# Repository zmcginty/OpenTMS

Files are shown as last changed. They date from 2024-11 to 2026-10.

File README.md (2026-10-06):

# Open-Source Transcranial Magnetic Stimulator

An open-source transcranial magnetic stimulator (TMS) project, including coil designs, pulse-generator hardware, and control/charging circuitry.

> **Safety Notice**
> This is **not** a legitimate medical device and is not a substitute for real TMS treatment. This is an experiment I built in my garage, and I cannot verify that it does what it's supposed to (if anyone wants to build an open-source MRI.... let me know...) This device is dangerous, it operates at energy levels more than enough to stop your heart, kill you, blow up and do lots of damage. If you're going to play with high energy pulsed power systems; be careful.

## Table of Contents
- [TMS Coils](#tms-coils)
- [Coil Cooling](#coil-cooling)
- [Coil Materials](#coil-materials)
- [IGBT Switches](#igbt-switches)
- [Gate Drivers](#gate-drivers)
- [Measurement System](#measurement-system)
- [Charging Circuit](#charging-circuit)
- [Pulse-Generator Designs](#pulse-generator-designs)
- [Charge-Control Circuit](#charge-control-circuit)
- [Useful Resources](#useful-resources)
- [TODO](#todo)

---

## TMS Coils

I primarily build two coil geometries — single coils and figure-8 coils. What I've focused on are air-core windings in either single-layer or multi-layer form. The general architecture is adapted from research papers and the limited information published by commercial TMS coil manufacturers. The figure-8 CloudTMS coil (below) was a major influence on my designs in terms of hollow copper conductor carrying coolant.

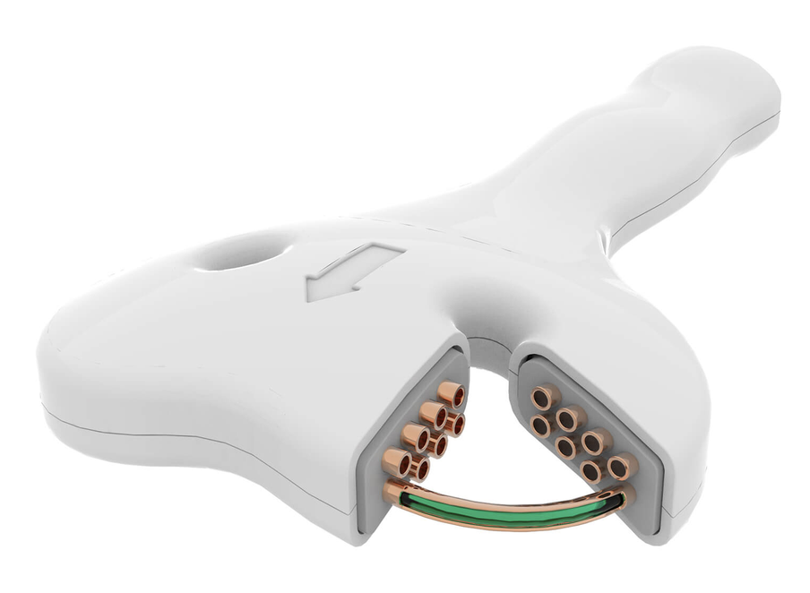
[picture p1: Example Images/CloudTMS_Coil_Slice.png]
CloudTMS coil


As I moved to higher pulse rates and energies, active cooling became necessary. My preferred approach, similar to the CloudTMS design, uses hollow copper tubing (sold for HVAC/refrigeration) insulated with PTFE heat-shrink. PTFE works well because it's a good dielectric, stays thin-walled after shrinking, tolerates high temperatures, and holds the coil shape better than thicker heat-shrink alternatives — though it does require fairly high heat to shrink fully.

**Build process:**
- Source 4mm OD / 3mm ID copper tube (5m sections) and 4.5mm, 4:1 PTFE heat-shrink in bulk.
- Feeding heat-shrink onto a long tube run takes patience — compressed air, used to create an air cushion between tube and shrink-wrap, makes this much easier.
- Wind the coil on a custom jig, either single-layer or multi-layer (multi-layer here just means winding randomly around a bobbin rather than stacking discrete single-layer coils).
- Insert something into the copper tube close to the tube's ID (weed-wacker cable works well) during the first few windings to prevent the tube from collapsing, then remove it once winding is complete.
- Hold the coil together with tape ahead of potting.

<p align="center">
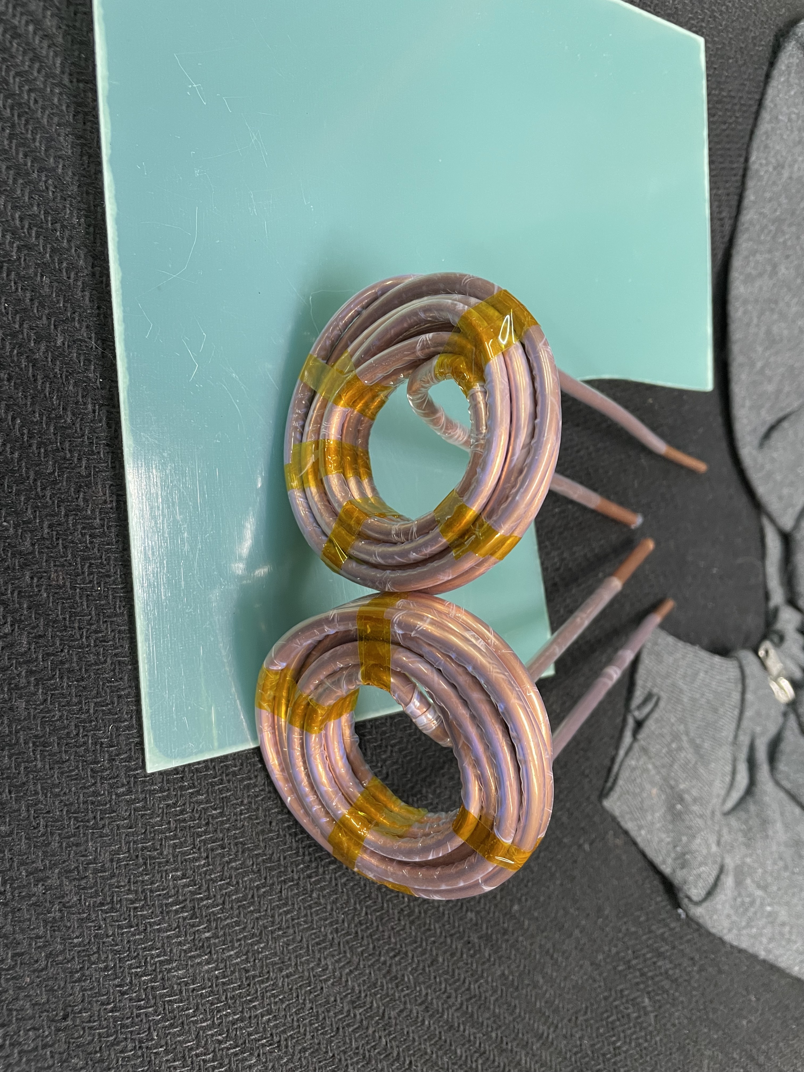
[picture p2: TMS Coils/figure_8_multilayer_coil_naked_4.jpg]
Coil before potting
  
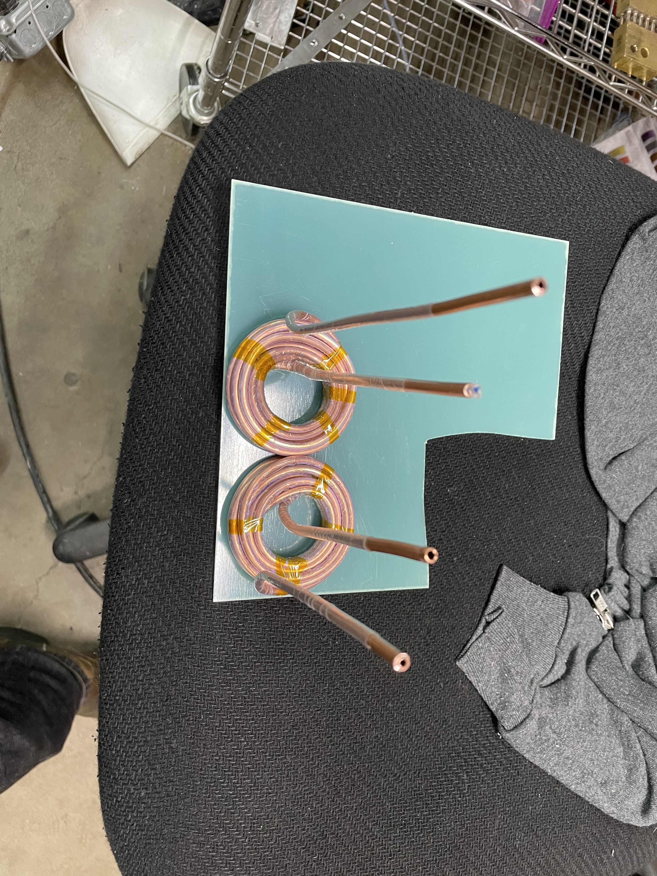
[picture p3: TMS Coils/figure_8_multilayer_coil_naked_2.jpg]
Coil before potting
  
</p>
<p align="center"><em>Example coil before potting</em></p>

Potting the coil in epoxy significantly improves mechanical stability and reduces noise by keeping the windings from moving against each other under pulse forces. Hot glue works as an alternative but produces coils that are noticeably louder in operation — not confidence-inspiring at higher power levels.

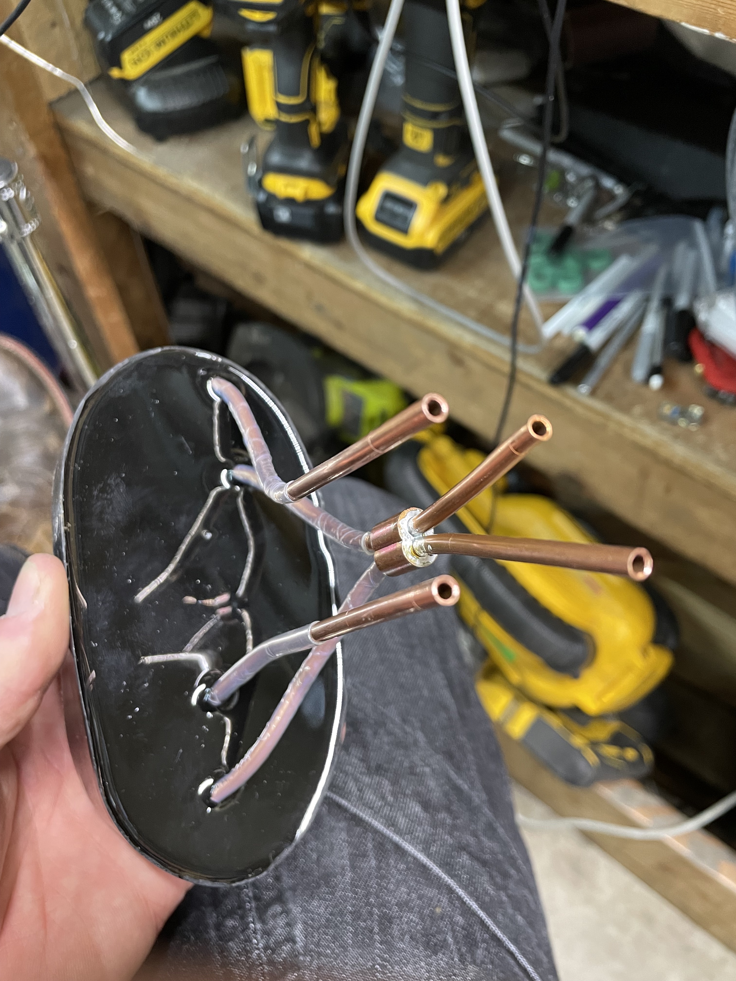
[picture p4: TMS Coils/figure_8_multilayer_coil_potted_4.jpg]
Coil after potting

<p align="center"><em>Example coil after potting</em></p>

## Coil Cooling

Coils built from hollow copper tube are cooled by pumping coolant through the winding itself.

- **Mineral oil:** Used for a long time — thinner than typical oils but thicker than water. Maintaining ~40°C required roughly 150–200 psi to push enough flow through the coil's small ID. At higher energy levels, I added a water chiller and heat exchanger to pre-cool the oil.
- **Distilled water:** More recently, I've switched to distilled water paired with a diaphragm pump, since the diaphragm provides a degree of electrical isolation between the pump mechanism and the fluid. This is simpler and more effective overall, though there is still a risk of the coolant loop reaching high voltage.

## Coil Materials

| Material | Purpose | Notes |
|---|---|---|
| [Hollow copper tube](https://www.amazon.com/dp/B082FDVNC5) | Water-cooled coil winding | Standard refrigeration-grade tube; cheap and widely available |
| [Fiberglass resin sheet](https://www.amazon.com/dp/B0DYT28W8W) | Application-side coil face | Sturdy, good electrical insulator, and appears permeable to magnetic fields — a disassembled commercial coil used what looked like FR4 fiberglass (PCB-grade) |
| [MAX EPC epoxy potting compound](https://www.amazon.com/dp/B07PMTMKZQ) | Coil potting | Inexpensive, good electrical insulator, decent thermal conductivity. For tube-cooled coils, MAX MCR (lower thermal conductivity) is also an option |

---

## IGBT Switches

My current switch of choice is the **Infineon/Eupec FZ1200R33KF2** — inexpensive and capable of handling substantial power. Prices on eBay range from ~$100–$400, and I've pushed 8kA pulses through a single unit. Adequate snubber capacitance/circuitry is essential to keep the voltage across the device under its 3.3kV rating (I target a safety margin below that).

## Gate Drivers

I've used two Power Integrations gate drivers with this IGBT:

- **2SC0535T2G0-33** — Functional, but lacks features like active clamping to protect against turn-off voltage spikes. Requires a custom PCB with gate turn-on/turn-off resistors and capacitors.
- **1SD418F2-FZ1200R33KF2** — Purpose-built for the FZ1200R33KF2; bolts directly onto the device pads. Requires only a 15VDC supply (I use a 1A source). It communicates over two fiber-optic channels (input signal and output/status), which I drive with custom PCBs using AFBR-1624Z HFBR transmitter/receiver modules, controlled by a Teensy 4.1 through a 3.3V→5V level shifter.

---

## Measurement System

### Differential Voltage Measurement
Monitoring Vce (collector-emitter voltage) across each IGBT is critical to staying within its rating — I keep a safety margin and stay below 2.5kV on 3.3kV-rated devices. Since these switches operate on the high side, measurement requires a high-voltage differential probe: I use a **Micsig DP20003** (5600V, 100MHz). A similar, lower-range HV differential probe (1300V) monitors the main capacitor bank voltage.

### Current Measurement
A shunt resistor was my first attempt but never produced a trustworthy signal. Two methods have worked well since:

1. **Rogowski coil** — Excellent for high current measurement (AC or DC, no iron core to saturate), but calibrated probes are hard to find secondhand, and a calibrated integrator circuit is needed to get a usable scope signal. I use a calibrated coil from [PowertekUK](https://powertekuk.com) — specifically the [CWTMini](https://powertekuk.com/cwtmini).
2. **Current transformer (CT)** — I use a Tektronix A621 AC current probe (rated to 2kA, available on eBay for $100–$500). In practice, it agrees with the Powertek Rogowski coil up to roughly 8kA despite the rated limit.

---

## Charging Circuit

The charging circuit is a simple, open-loop design: mains power feeds a variable transformer (variac), which drives a microwave oven transformer (MOT) to step up voltage. The stepped-up AC is rectified by a full-bridge rectifier and used to charge the main discharge capacitor bank, which is then discharged through the coil via a high-side switch (latching SCR or non-latching IGBT).

### Microwave Oven Transformers
The current two-switch flyback pulse generator uses two matched MOTs (matched by checking voltage and phase agreement between units — *measurements/resources TODO*). Drawing ~15A at 120V, two matched transformers stay below ~60°C with air cooling alone.

Earlier designs used a single MOT with low-pressure mineral-oil cooling, which worked up to ~14A — but oil cooling systems and pumps added complexity and were prone to leaks.

---

## Pulse-Generator Designs

### Design #1 — SCR-Based Pulse Generator
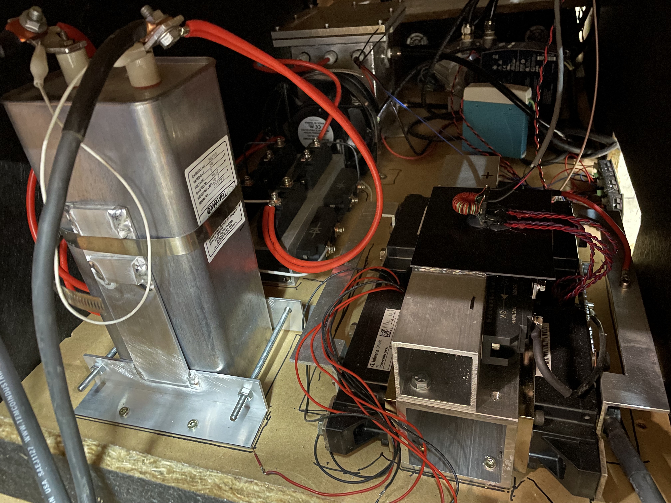
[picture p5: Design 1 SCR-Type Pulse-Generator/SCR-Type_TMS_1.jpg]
SCR switch bottom-right

<p align="center"><em>SCR-switch pulse generator (SCRs are bottom-right. Main capacitor front left. Rectifier behind capacitor. and mineral-oil cooled microwave transformer behid rectifier. </em></p>

The first design I built. It handles very high energy levels well at consistent frequencies/patterns (e.g., the standard 5Hz/10Hz protocols used in early depression-treatment research). Its limitation is pattern flexibility: an SCR/thyristor is a latching switchable diode, so once triggered it fully discharges the capacitor. This steady current decay is gentle on flyback effects but rules out more complex patterns like Theta-Burst (50Hz bursts repeating at 4–5Hz).

### Design #2 — Single-IGBT Pulse Generator
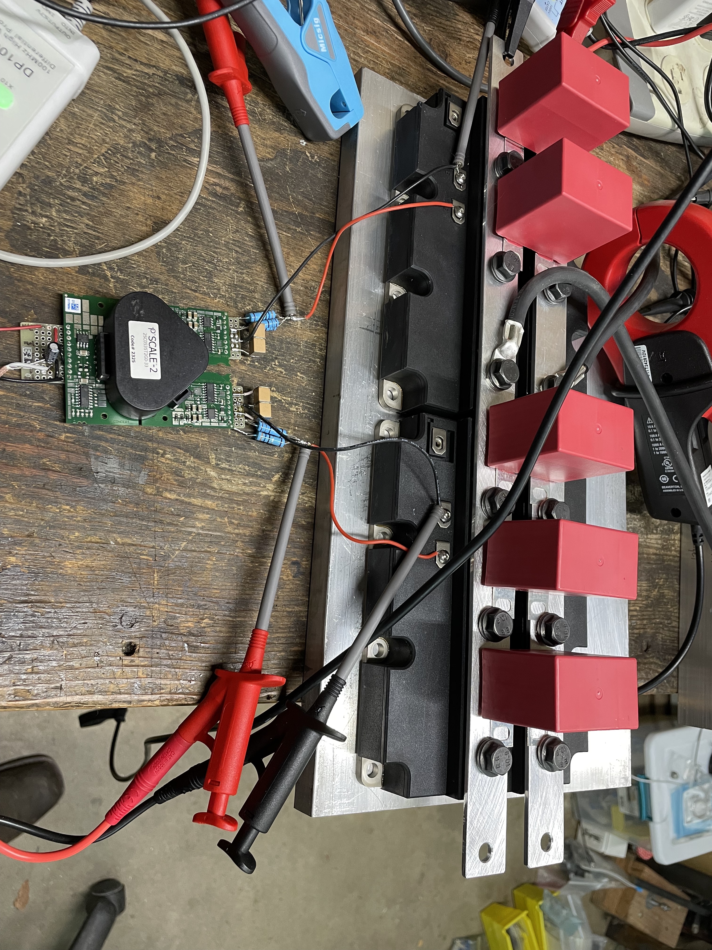
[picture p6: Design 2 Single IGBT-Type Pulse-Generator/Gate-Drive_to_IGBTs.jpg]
Single-IGBT (Two IGBTs in parallel)

<p align="center"><em>Single IGBT topology (note; two IGBTs in parallel), you can also see gate driver I used before using ones built specifically for the IGBT module</em></p>

Since IGBTs aren't latching, they can be switched on and back off within a short pulse, allowing partial capacitor discharge and enabling patterns like Theta-Burst. The tradeoff is significant flyback voltage when interrupting current through the coil — this destroyed several IGBTs before I addressed it with a robust flyback diode across the coil and snubber capacitors across the IGBT(s) to absorb spikes from parasitic wiring/busbar inductance. HV differential probes are essential here to stay within the switch's voltage rating while tuning.

This design uses a flyback diode across the coil, producing a sharp current rise but a slow fall (as flyback energy dissipates through coil/wire resistance and the diode). It worked well and was relatively simple compared to the two-switch flyback design, but since flyback energy isn't recycled, it's ultimately limited by the 120V/15A charging circuit.

### Design #3 — Two-Switch Flyback IGBT Pulse Generator
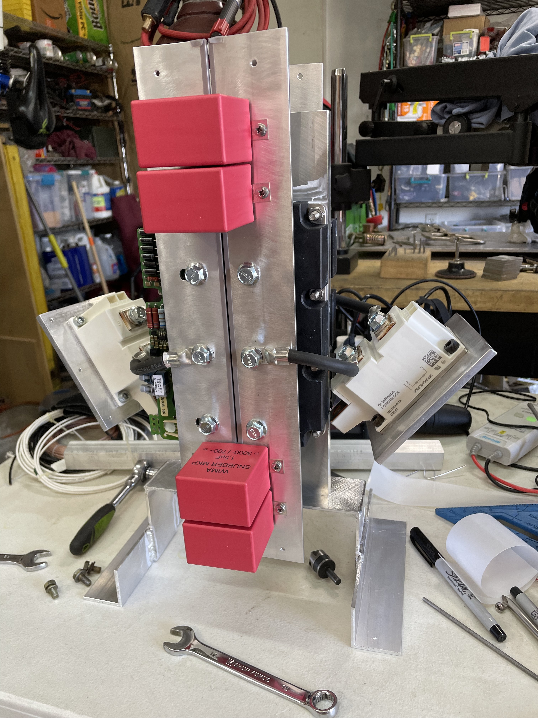
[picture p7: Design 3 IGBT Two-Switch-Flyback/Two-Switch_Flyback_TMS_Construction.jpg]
Construction of Two-Switch Flyback

<p align="center"><em>Two-Switch flyback topology being built. You can see the diodes hanging off to the sides. And gate drives are now on the left, bolted to IGBT modules behind bus-bars.</em></p>

This design recycles more pulse energy than the single-IGBT version and produces both a sharp rising *and* falling current edge, increasing di/dt for a stronger but shorter magnetic field pulse. It noticeably reduced charging-circuit current draw and appears more effective at stimulating muscle/nerve tissue than the single-switch design, even at higher peak current — likely because faster field transitions induce greater current in tissue.
+ For this design it's important to thermally bond both IGBT/switch modules so that they're the same temperature and have the same switching characteristics. For this I bolt them each to opposite sides of an aluminum plate which I attach water-cooling blocks to.
I've been realizing the importance of keeping switching loops tight, and have shortened cabling from capacitor to IGBTs, and shortening cables from IGBTs to diodes.
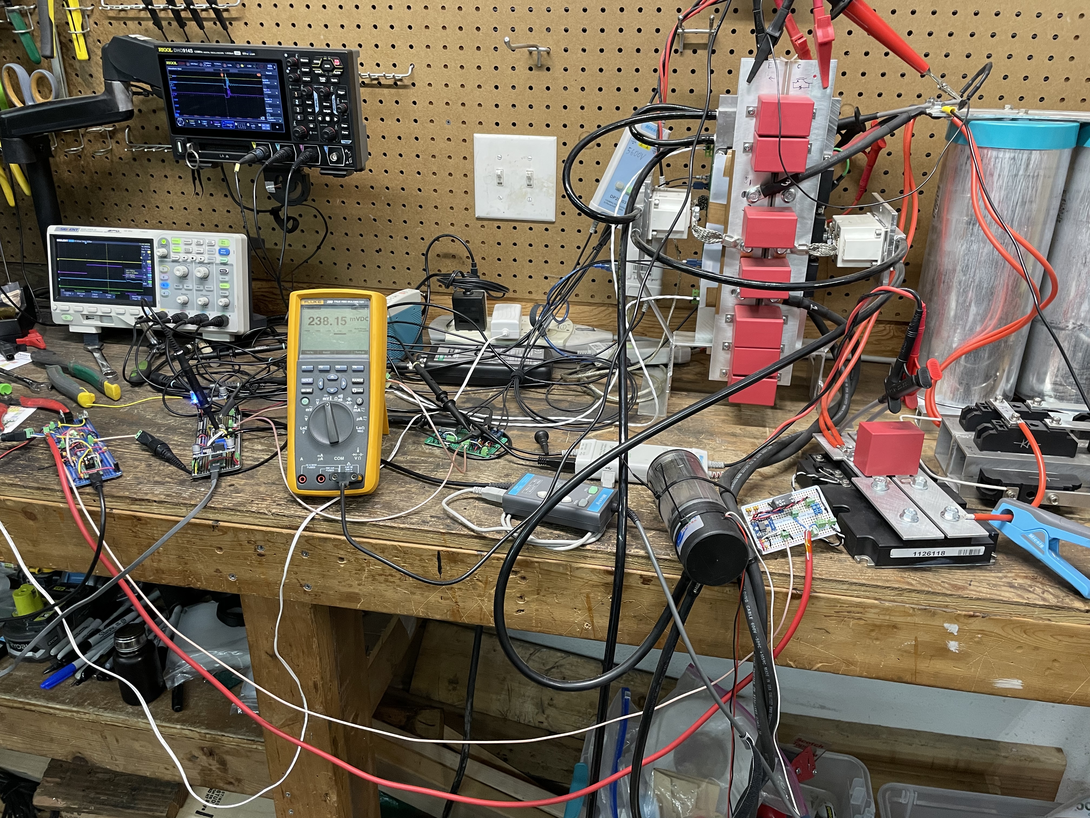
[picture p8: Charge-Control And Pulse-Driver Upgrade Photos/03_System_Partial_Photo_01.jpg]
System Photo

<p align="center"><em>Photo of the system, from left-to-right; charge-control board, multimeter, main pulse-IGBTs (with many red snubber caps), charge-control IGBT (with single red snubber in front), charge-circuit-rectifier, and main pulse capacitor bank in back </em></p>

### Design #4 — H-Bridge IGBT Pulse Generator (Not Yet Built)
Should double coil pulse current relative to the two-switch flyback topology by enabling current reversal. The complexity of positioning four large IGBT switches and the associated snubbers and diodes close to eachother, with cooling is going to be difficult without adding parasitic inductance that would offset the gains.

---

## Charge-Control Circuit
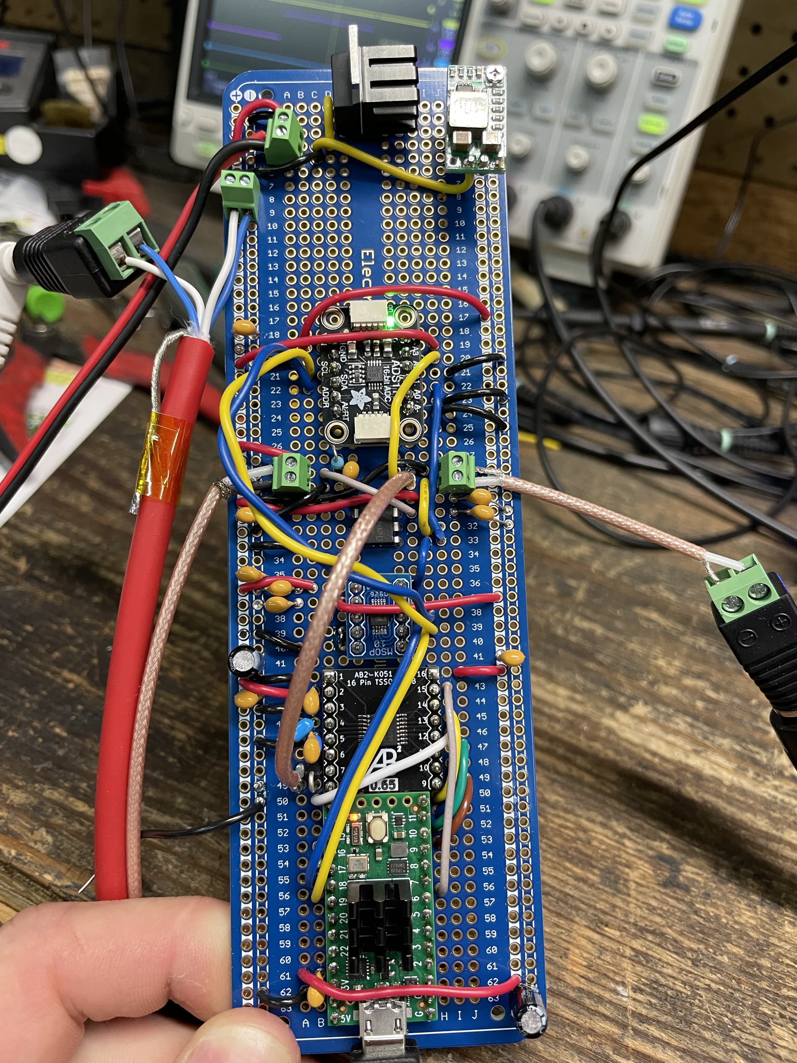
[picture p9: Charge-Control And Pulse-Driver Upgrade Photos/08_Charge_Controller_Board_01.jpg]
Newly-Built Charge-Controller Board

<p align="center"><em>Newly Built Charge-Control Board with (from bottom to top) Teensy 4.0, ADS8699 high-speed ADC, AD5693 DAC, LM393P Comparator, ADS1115 4ch slow ADC, 5V LDO, and 3.3V buck-converter</em></p>

The new charge-control system seems to be working well enough for calling it version 1!!! After many failed attempts to measure a voltage divider, and my ground plane shifting and making either the teensy and/or ADC shit itself, even after adding digital SPI isolators, I realized.... that's what HV diff probes are for! So ripped out some HV SPI/I2C isolators and I'm now just measuring the output of a Micsig 1300v diff probe. No glithes, no isolators causing signal delays, no fried chips and salsa. Perfect.

The new approach uses a DAC to output a reference voltage into a comparator, which compares it against the output of the Micsig 1300v differential probe. I have probe scale-factors in the teensy code as well as linear calibrations for both ADCs and DAC as well. I have the fast ADC on here as well incase I want to control the charge-circuit via the teensy reading ADC instead of from the comparator + DAC, but for now the comparator + DAC method is working great, so we have some extra/redundant ADCs. A weak pull-down on the DAC output ensures that if the microcontroller glitches or crashes, the DAC voltage falls to zero and the charge circuit fails safely.

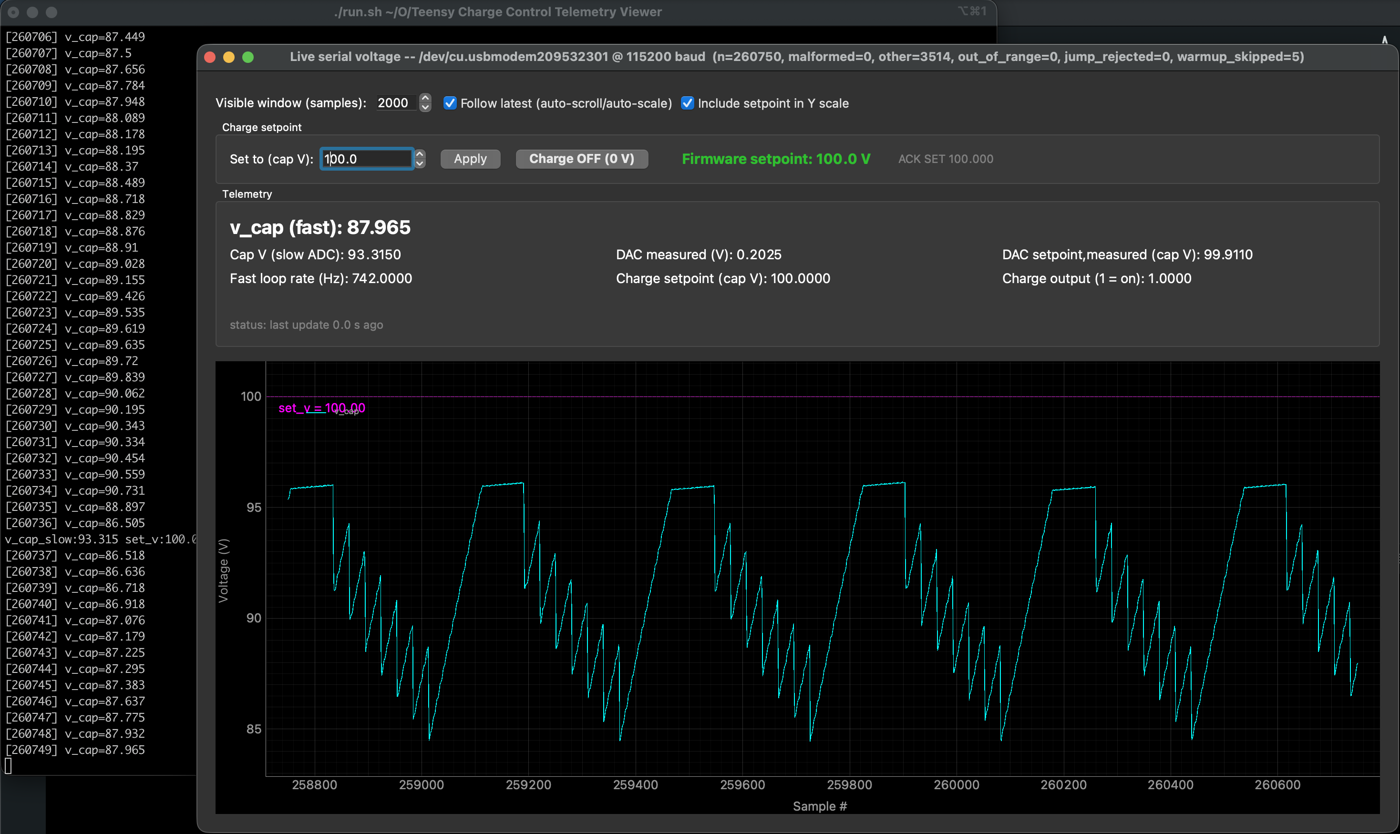
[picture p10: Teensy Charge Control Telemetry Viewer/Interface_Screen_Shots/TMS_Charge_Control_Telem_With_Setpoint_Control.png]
Python Telemetry Graph/Display

<p align="center"><em>Screenshot of a python script which displays a realtime graph and telemetry from the serial output of the teensy charge-control. Also added the ability to adjust the charge-setpoint in the python window. You can see the pulse trains as the capacitor discharges, and the charge controller working as it limits the capacitor voltage at the setpoint of (close to) 100V!</em></p>

Above is a screenshot of a python script which listens to voltage values sent over serial from the teensy charge controller and will display a live graph of the capacitor voltage, which is really useful for debugging as it's basically an autoscaling slow oscilliscope. The graph only shows the fast ADC's (ADS8699) calibrated capacitor voltage. It also displays other, slow-speed telemetry as numbers such as the slow ADC's calibrated capacitor voltage, slow ADC's measurement of DAC's output in both raw voltage, and the scaled/calibrated set-voltage it corresponds to (ie. I set the DAC to output a voltage which corresponds to 200V from the Micsig, I can verify that the ADC's measurement reads close enough, like 199.2V) I also added control to adjust the voltage setpoint from this python window which is useful for testing system starting from low voltage to be safe. I think there may be something with the comparator which is causing the cutoff to be slightly below the setpoint; in the screenshot you can see it cutting at ~95V instead of 100V. More calibrations....

## Upgrades to Pulse-Driver system
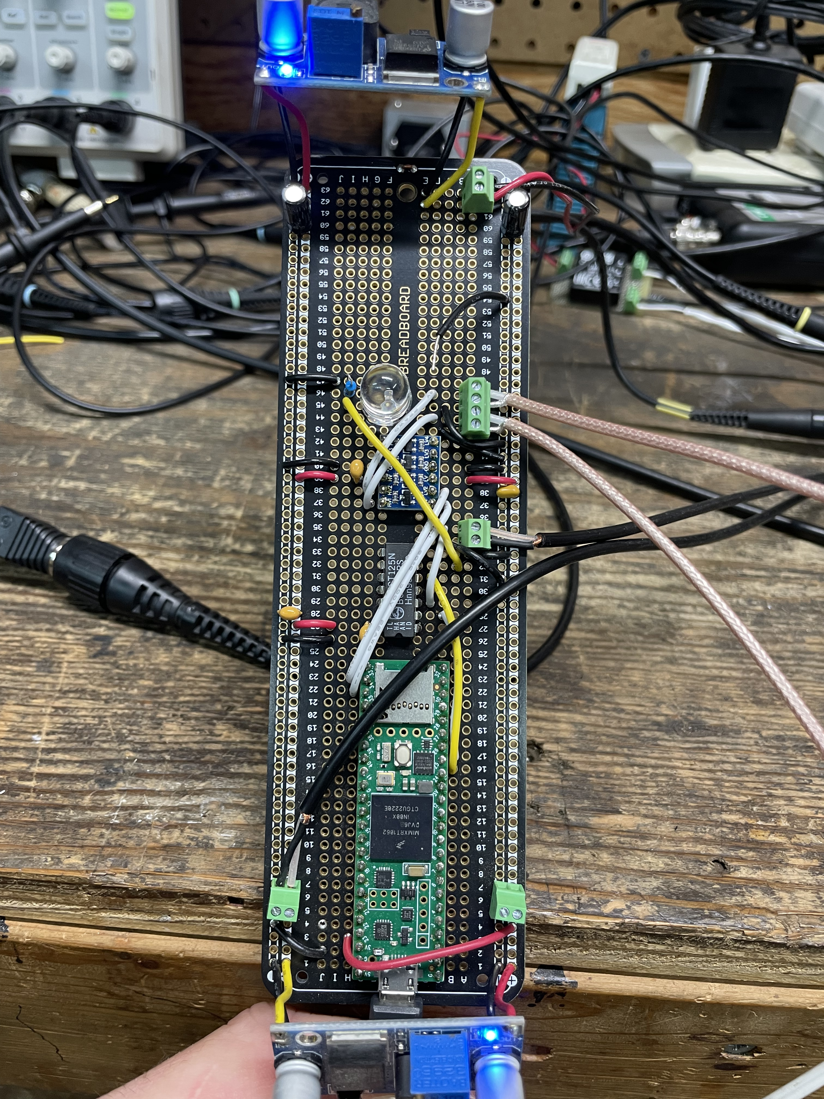
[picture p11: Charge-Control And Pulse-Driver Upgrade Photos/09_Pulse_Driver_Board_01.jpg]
Upgraded Pulse-Driver Board

<p align="center"><em>Pulse Driver Board with added inputs for RX signals from fiber-optic interface board, level-shifter and fault LED</em></p>

I've made some additions to the pulse-driver control circuit as well; for a while I was just sending pulses from the teensy to the fiber-optic transmitters to fire the IGBT switches, and not reading the signal received from the other fiber line which acknowledges the driver received each pulse, and can indicate faults like a short-circuit. I wired up the fiber RX lines, ran them through a level shifter to 3.3v for the teensy to read and the teensy is now checking that each pulse was ack'd by each gate-driver, and can turn on the big-red fault LED if something's wrong. NOTE: Big-Red Fault LED will blink if the teensy detects a warning; like a an ack pulse was slightly off, or short/long. The LED will latch on if it detects a fault such as a short-circuit. It also prints this data + occasional status out over serial. The teensy code has the ability to control a safety relay to shut off main power to the system if a fault is detected, but I don't have that safety mechanical relay wired in yet, so for now, it just keeps going.

---

## Safety Resources
- [TMS Safety with respect to seizures](https://pmc.ncbi.nlm.nih.gov/articles/PMC7732158/pdf/ndt-16-2989.pdf)
- [General article discussion factors which can decrease seizure-threshold (make it more likely you'll have a seizure)](https://www.wmchealth.org/living-well/7-everyday-factors-that-can-increase-seizure-risk)
- [Concise overview from clinic of seizure risk factors](https://www.midcitytms.com/transcranial-magnetic-stimulation-safety-with-respect-to-seizure-ndt/)

## Useful Resources

- [Online calculator used for Beam-Protocol/10-20 system to calculate position of DLPFC](https://clinicalresearcher.org/F3/calculate.php)
- [Same online calculator, where you enter your measurements](https://clinicalresearcher.org/F3/)
- [Clinical Researcher Software Tools (where I got the two links above) Contains other tools that could be useful for motor-threshold stuff](https://clinicalresearcher.org/software.htm)

## Useful Videos
- [Coil placement and the 10-20 system/beam protocol (video)](https://youtu.be/CKCvAkgdJuY?si=6TRw3_EgRK5eAh5G)
- [Same video as above with added instructions to enter measurements into clinicalresearcher calculator (link above)](https://youtu.be/akp4V5PFb6A?si=kvKB5cpgHWPCvdm8)
- [Good introductory explanation of general TMS](https://www.youtube.com/watch?v=NQHVfF_5rtc)
- [Funny video of the TMS researcher interrupting his speach with TMS](https://www.youtube.com/watch?v=85QKdt8boMA)
- [Researcher showing TMS stimulating muscles directly and muscles through the motor-cortex](https://www.youtube.com/watch?v=JA0q4fVqrFQ)
- [Good Long-Form explanation of someone who runs a TMS clinic showing how they get a patient setup, and perform treatment](https://www.youtube.com/watch?v=WxCunEG2oi0)

## TODO
1. **UPDATE THE SCHEMATICS**
2. **Refine charge-control switch** The charge controller is working well now. But I'm using a rediculously big IGBT to switch just a few tens of amps. Need to find a smaller IGBT/switch which can withstand ~2-3kV.
3. **Build a phase-control rectifier** to replace the HV charge circuit's current rectifier and eliminate the variac, integrating it into the charge system. May need PID-style control of phase/firing angle — or a simpler bang-bang control scheme.
4. **Process gate-driver fault feedback** Reading status/feedback from gate-drivers is working now and has latching/blinking LEDs/indicators to indicate warnings and faults. There is functionality to turn off a safety relay, disconnecting power from a subsystem or whole system which I'll get wired up later.
5. **Add functionality to Pulse-Driver** To run different patterns/protocols, maybe add input (with damn good shielding) so user can press a button to fire a single pulse.
6. **Finally build a tool to map the magnetic field strength & shape of a coil.** My idea is basically put a precise analog hall-effect sensor on some 3d gantry machine like a 3d printer, and have it scan over many 3d points around the coil and create a 3d heat-map of magnetic field strength. Anyone know how to use 3d-printers? and know how to make them scan some end-effector to create a map like this???? I'd love some help!

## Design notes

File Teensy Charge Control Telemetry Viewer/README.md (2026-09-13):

This is a sub-project of the pulse-generator; a charge controller arduino sketch for reading an ADC to read divided capacitor voltage, and toggling an output to turn on or off the charge circuit. No fancy porpotional control yet...

There's also a python script which takes in voltage values from a serial port and plots them using pyqtgraph lib in real-time and can log data for analysis. This is basically for tuning the ADC system given how noisy the environment is around this pulse-generator. So it allows me to tune how I average ADC samples and so on, so I don't get any major jumps or noise.

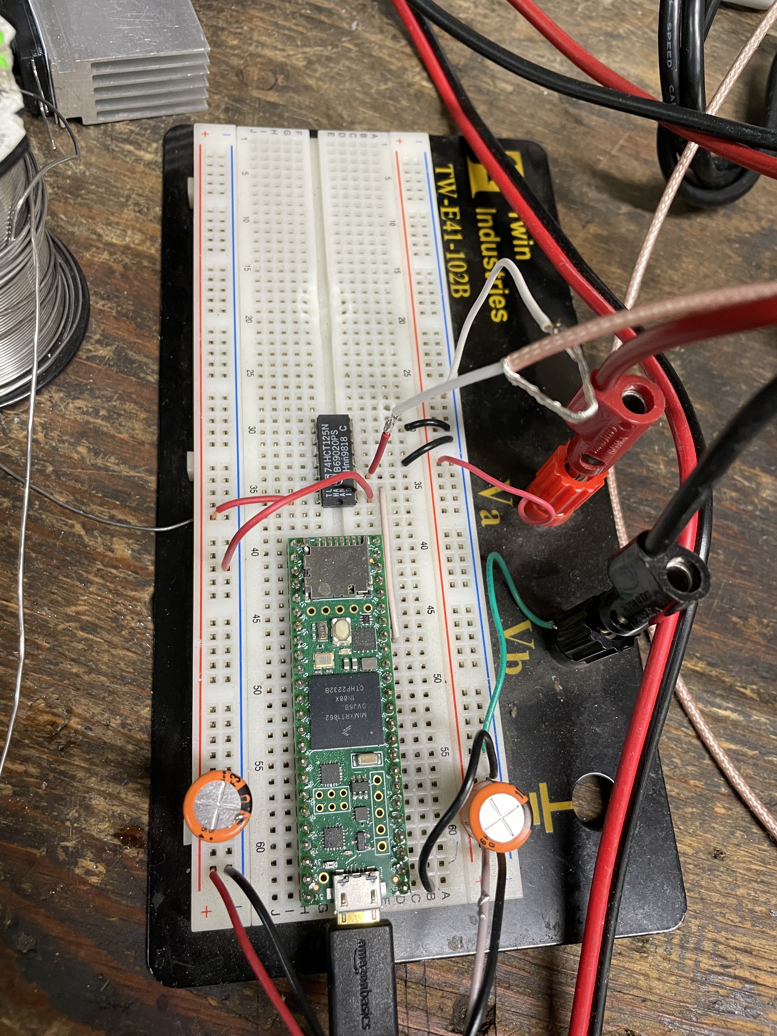
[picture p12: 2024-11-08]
Design 2 Single IGBT-Type Pulse-Generator/Teensy_Pulse-Gen_with_Level_Shift_2.jpg

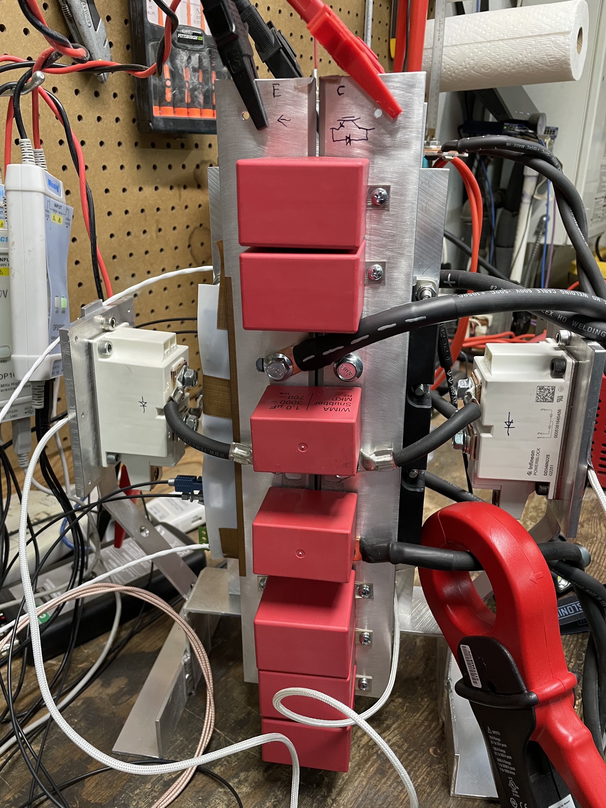
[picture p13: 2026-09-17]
Design 3 IGBT Two-Switch-Flyback/Two_Switch_Flyback_TMS_1.jpg

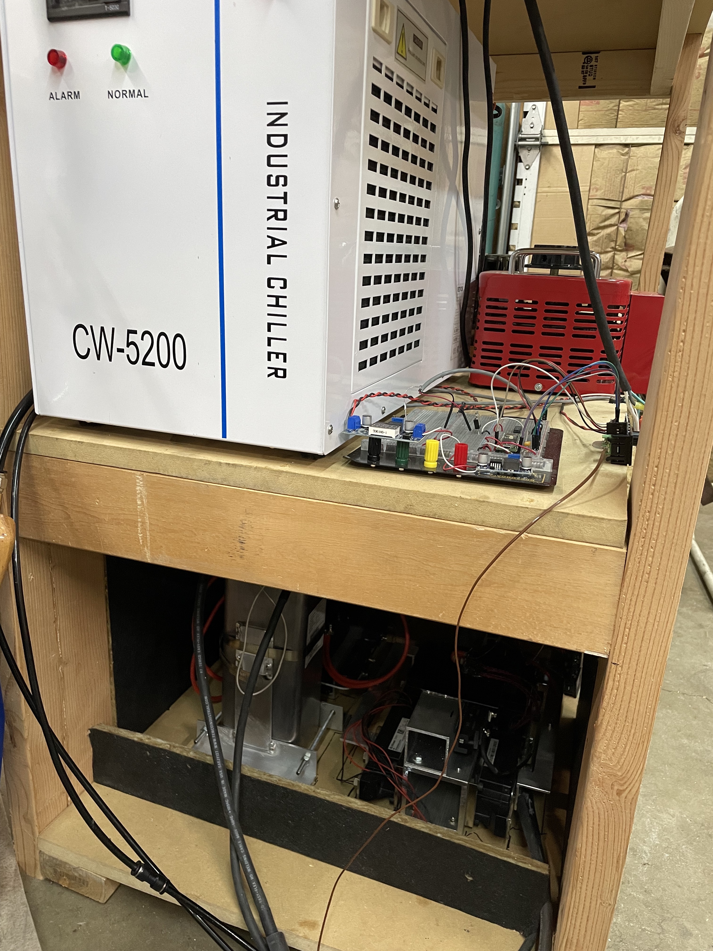
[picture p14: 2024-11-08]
Design 1 SCR-Type Pulse-Generator/SCR-Type_TMS_Power_Cooling_Control.jpg

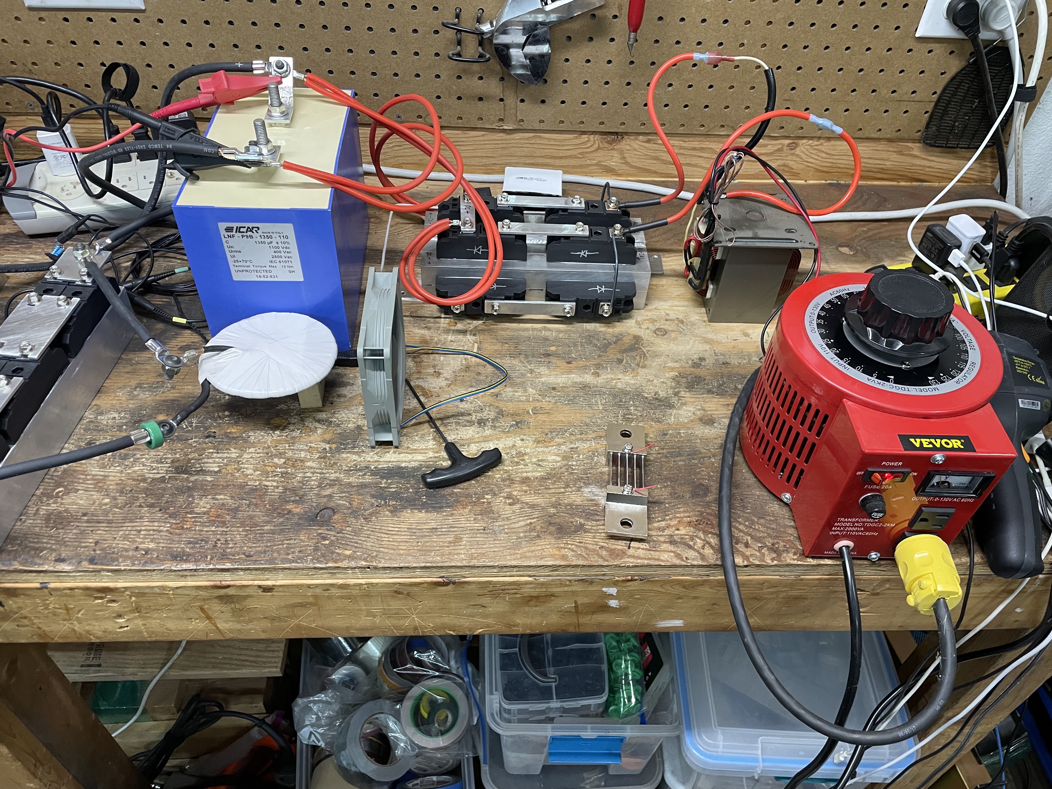
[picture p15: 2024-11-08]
Design 2 Single IGBT-Type Pulse-Generator/Charging_Circuit_1.jpg

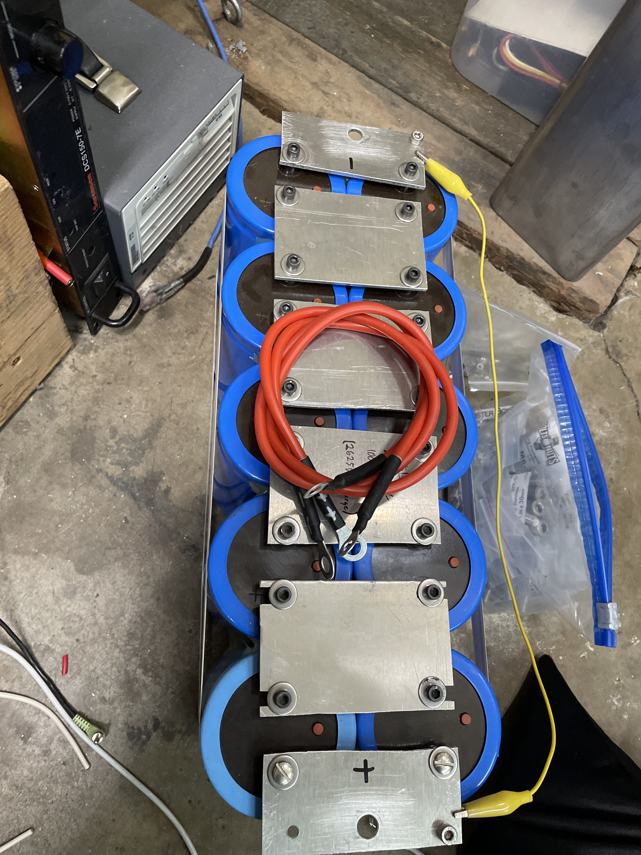
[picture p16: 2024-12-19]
Design 2 Single IGBT-Type Pulse-Generator/electrolyt_cap_bank.jpg

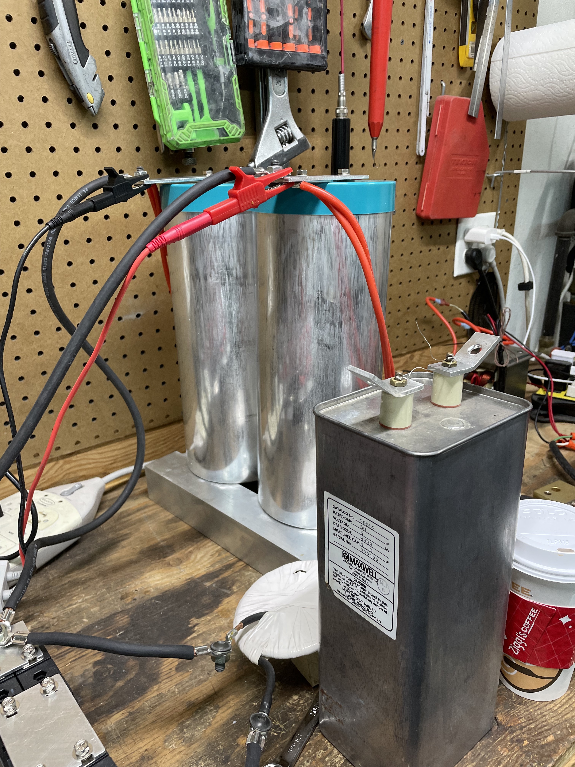
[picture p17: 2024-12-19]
Design 2 Single IGBT-Type Pulse-Generator/4kv_oil_cap_next_to_1800v_film_caps.jpg

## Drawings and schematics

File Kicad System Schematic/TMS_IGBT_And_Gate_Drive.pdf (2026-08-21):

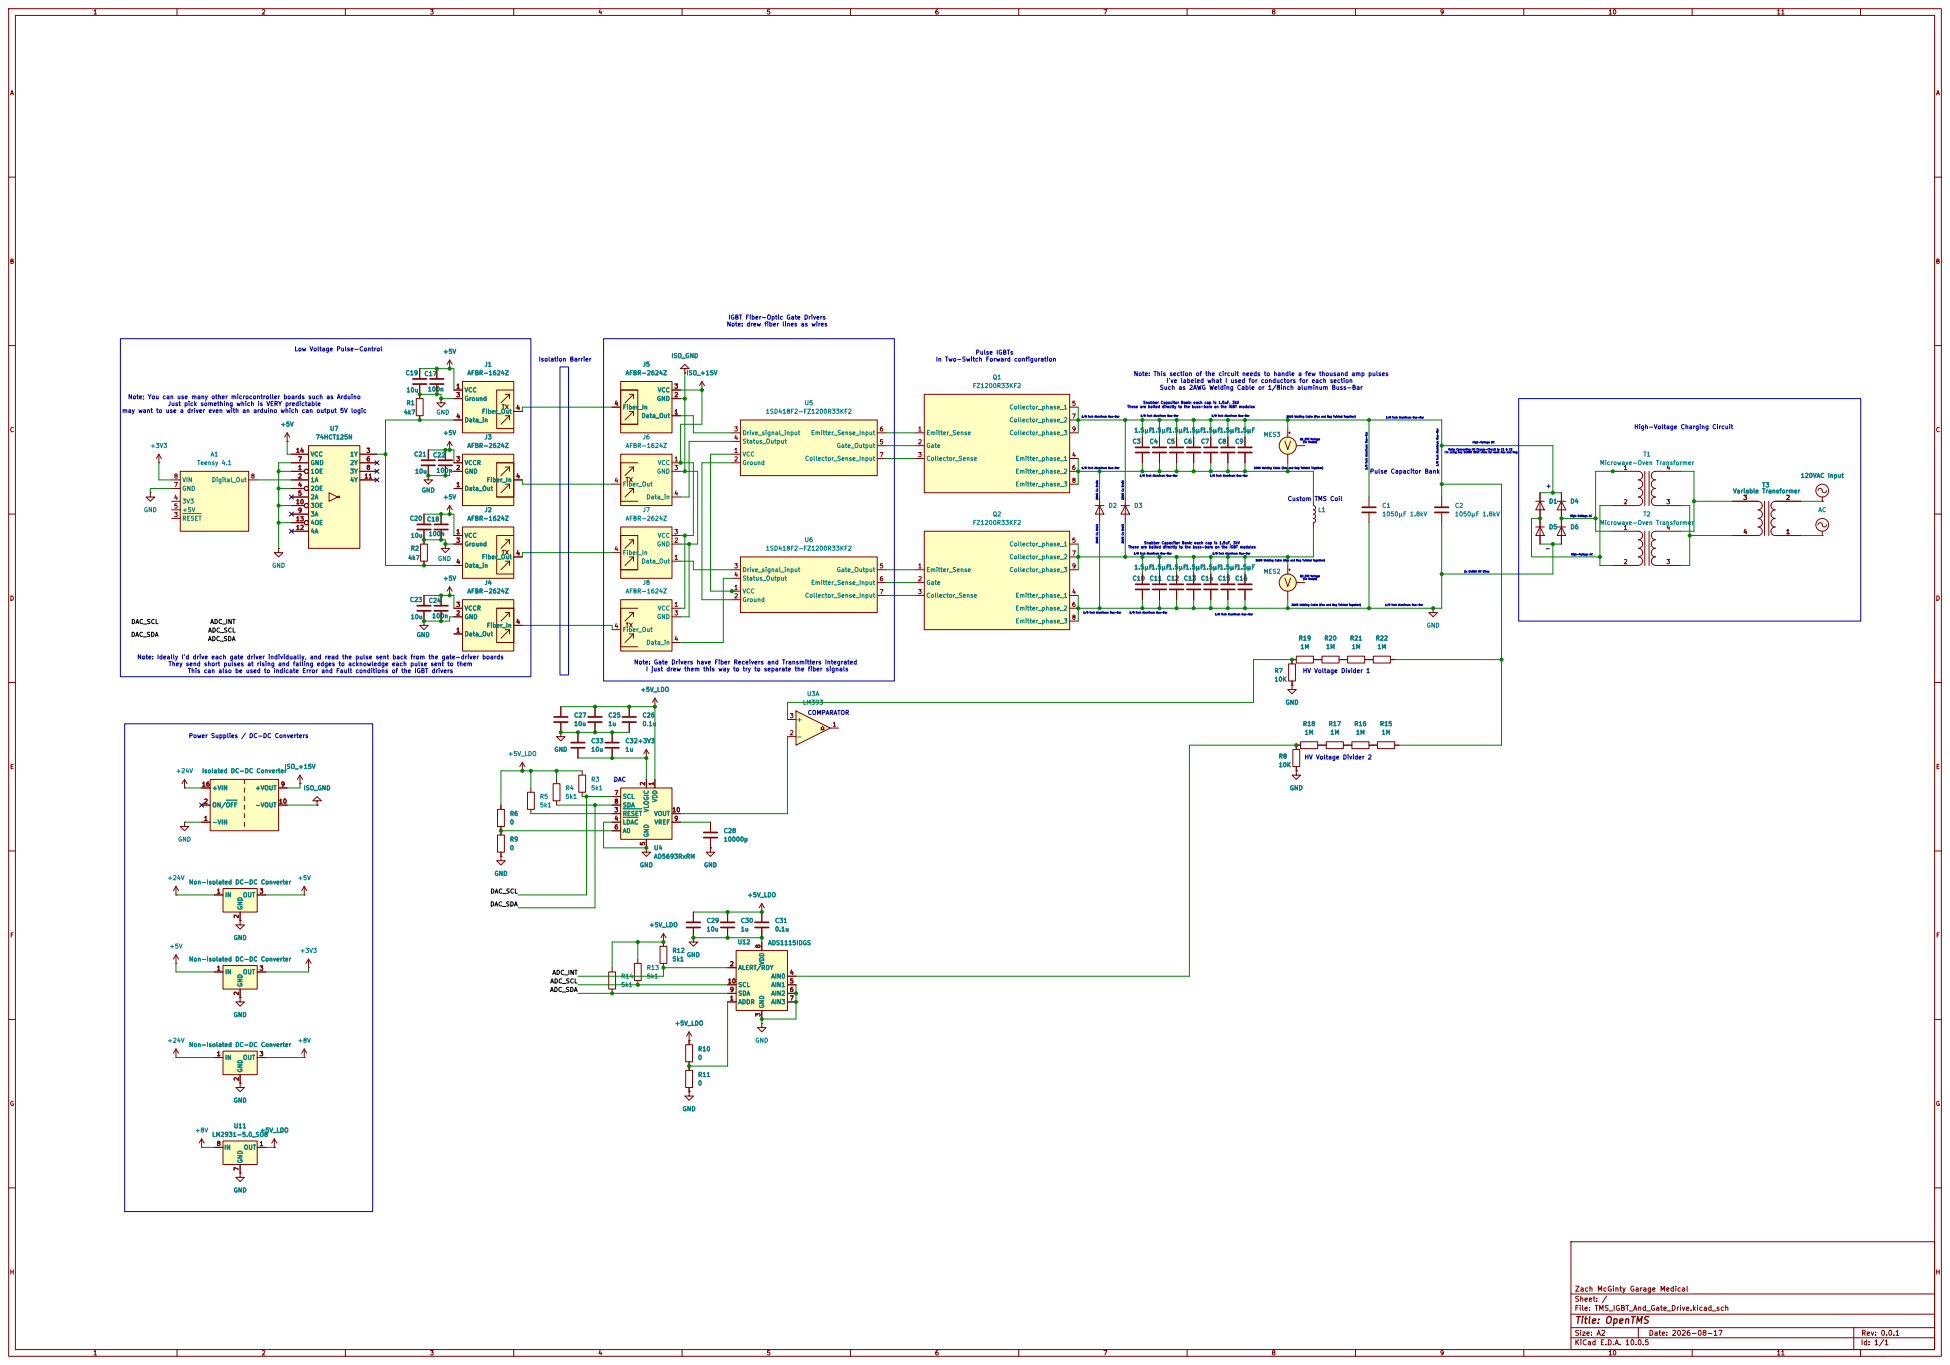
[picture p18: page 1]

IGBT Fiber-Optic Gate Drivers Note: drew fiber lines as wires
AFBR-2624Z R6

1/8 inch Aluminum Bus-Bar Pulse Capacitor Bank1/8 inch Aluminum Bus-Bar 1/8 inch Aluminum Bus-Bar Isolation Barrier

1/8 inch Aluminum Bus-Bar Note: This section of the circuit needs to handle a few thousand amp pulses

I've labeled what I used for conductors for each section Such as 2AWG Welding Cable or 1/8inch aluminum Buss-Bar

1/8 inch Aluminum Bus-Bar Note; You can use many other microcontroller boards such as Arduino
Just pick something which is VERY predictable may want to use a driver even with an arduino which can output 5V logic

These are bolted directly to the buss-bars on the IGBT modules

2AWG Welding Cable (Pos and Neg Twisted Together) Snubber Capacitor Bank; each cap is 1.5uF, 3kV

High-Voltage DC Note: Connecting HV Charge-Circuit to C1 & C2

I'm using two 14AWG 30kV wires for each Pos and Neg Note: Ideally I'd drive each gate driver individually, and read the pulse sent back from the gate-driver boards

T2 Microwave-Oven Transformer GND

High-Voltage AC Q2 Diff Voltage

2 OUT 3 Non-Isolated DC-DC Converter V

2AWG Welding Cable (Pos and Neg Twisted Together) Note: Gate Drivers have Fiber Receivers and Transmitters Integrated

They send short pulses at rising and falling edges to acknowledge each pulse sent to them

This can also be used to indicate Error and Fault conditions of the IGBT drivers

2 OUT 3 Non-Isolated DC-DC Converter R16

GND Non-Isolated DC-DC Converter

Isolated DC-DC Converter

2 OUT 3 GND Non-Isolated DC-DC Converter

2 OUT 3 Non-Isolated DC-DC Converter +5V_LDO C31

IN 8 Non-Isolated DC-DC Converter

Zach McGinty Garage Medical
Sheet: /
File: TMS_IGBT_And_Gate_Drive.kicad_sch
Title: OpenTMS

Size: A2 | Rev: 0.0.1
KiCad E.D.A. 10.0.5 | Id: 1/1

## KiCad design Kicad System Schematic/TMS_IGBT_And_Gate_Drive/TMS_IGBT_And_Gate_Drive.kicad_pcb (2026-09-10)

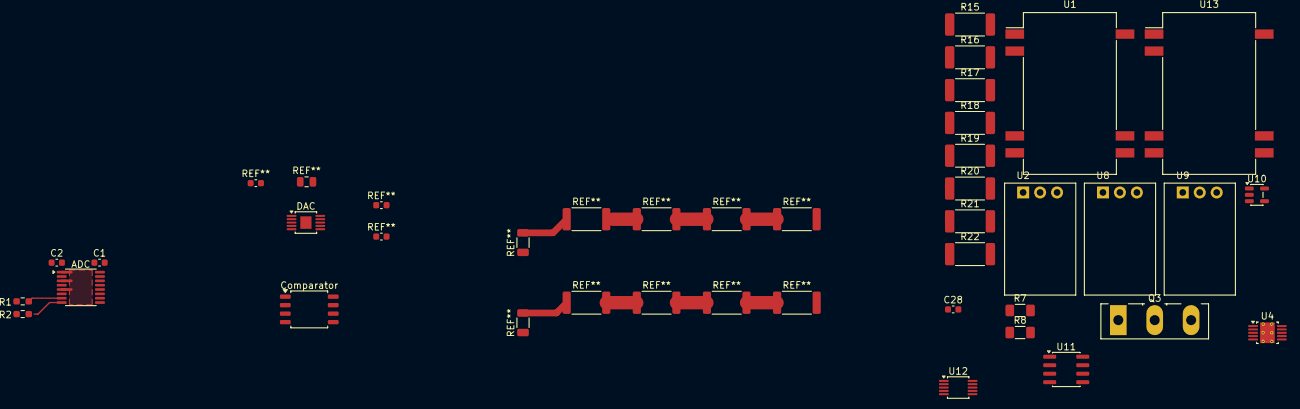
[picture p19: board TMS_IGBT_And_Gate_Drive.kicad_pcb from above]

Board: 2 copper layers, 28 parts (0 on the bottom side), 15 nets.

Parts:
ADC: ADS8699IPWR; TSSOP-16_4.4x5mm_P0.65mm
C1, C2: C_0603; C_0603_1608Metric
C28: 10000p; C_0603_1608Metric
Comparator: LM293DR; SOIC-8_5.3x5.3mm_P1.27mm
DAC: AD5683RARMZ; MSOP-10-1EP_3x3mm_P0.5mm_EP1.68x1.88mm
Q3: IRG4PF50W; TO-247-3_Vertical
R1, R2: R_0603_1608Metric_Pad0.98x0.95mm_HandSolder
R7, R8: 10K; R_1206_3216Metric_Pad1.30x1.75mm_HandSolder
R15, R16, R17, R18, R19, R20, R21, R22: 1M; R_2512_6332Metric_Pad1.40x3.35mm_HandSolder
U1, U13: Isolated DC-DC Converter; Converter_DCDC_Artesyn_ATA_SMD
U2, U8, U9: Non-Isolated DC-DC Converter; Converter_DCDC_Murata_OKI-78SR_Horizontal
U4: AD5693RxRM; AD5683RARMZ
U10: MCP1415; SOT-23-5
U11: LM2931-5.0_SO8; SOIC-8_3.9x4.9mm_P1.27mm
U12: ADS1115IDGS; TSSOP-10_3x3mm_P0.5mm

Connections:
+5V: U2.3 (OUT), U8.1 (IN)
+8V: U9.3 (OUT), U11.8 (IN)
+24V: U1.16 (+VIN), U2.1 (IN), U9.1 (IN), U13.16 (+VIN)
GND: C28.2, Q3.2 (C), R7.1, R8.1, U1.1 (-VIN), U2.2 (GND), U8.2 (GND), U9.2 (GND), U11.2 (GND), U11.3 (GND), U11.6 (GND), U11.7 (GND), U12.3 (GND), U12.5 (AIN1), U12.6 (AIN2), U12.7 (AIN3), U12.8 (VDD), U13.1 (-VIN)
ISO_+15V: U1.9 (+VOUT), U10.2 (Vdd), U13.9 (+VOUT)
ISO_GND: U1.10 (-VOUT), U10.4 (GND), U13.10 (-VOUT)
unnamed: R15.2, R22.2
unnamed: R15.1, R16.2
unnamed: R16.1, R17.2
unnamed: R17.1, R18.2
unnamed: R19.2, R20.1
unnamed: R20.2, R21.1
unnamed: R21.2, R22.1
unnamed: R7.2, R19.1
unnamed: R8.2, R18.1, U12.4 (AIN0)

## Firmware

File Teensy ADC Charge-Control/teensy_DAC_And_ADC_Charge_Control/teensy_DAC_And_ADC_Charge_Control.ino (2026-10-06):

/*
  OpenTMS Charge_Control, built to run on Teensy 4.0
    ADS8699 18-bit SAR fast ADC for reading capacitor voltage through Micsig Active H.V. Differential Probe
    AD5693 16-bit DAC outputs analog signal to comparator, which compares DAC output to voltage from Micsig H.V. Diff Probe (capacitor voltage)
    ADS1115 16-bit Sigma-Delta slow ADC for verifying DAC output, and as another redundant reading of Micsig H.V. Diff Probe (capacitor voltage)

  This control system can either
    1. Directly control connecting/disconnecting the capacitor's charge circuit by reading the capacitor's voltage, and turning off charge-circuit when it gets above a set threshold
    2. Or by outputting an analog signal via the AD5693 DAC which a comparator compares to the capacitor's voltage. I beleive the comparator is more robust and fail-safe.

  CHARGE SETPOINT (settable over Serial):
    One setpoint, in capacitor volts, drives both methods: the DAC/comparator
    threshold and the direct ADC control. It starts at 0 V (charging disabled)
    on every boot and can never exceed SETPOINT_MAX_V.
    Commands (one per line, case-insensitive):
      SET <volts>   set the charge setpoint, e.g. "SET 800"
      OFF           setpoint to 0 V (charging disabled)
      GET           report the current setpoint
      AVG <n>       ADS8699 averaging depth (NUM_AVG)
    Replies: "ACK SET 800.000", "ACK AVG 500", or "ERR <reason>".
    The status line also reports the active setpoint as "set_v:<volts>".

  LOOP STRUCTURE (cooperative multi-rate scheduling, no threads):
    - FAST path, every loop():  ADS8699 averaged read -> direct charge control.
    - SLOW paths, non-blocking, each on its own timer:
        dac_service()     -- writes the AD5693 only when the target code changes.
        ads1115_service() -- state machine: starts a conversion, comes back
                             later to collect it. Never waits on the ADC.
        command_service() -- reads serial commands, never blocks.
        print_service()   -- rate-limited Serial output.
    Each slow task does at most ONE short I2C transaction per loop() pass,
    so the fast path is never stalled for more than ~100-200 us by I2C.
*/

#include <SPI.h>
#include "Adafruit_AD569x.h"
#include <Wire.h>
#include <Adafruit_ADS1X15.h>

Adafruit_ADS1115 ads;
Adafruit_AD569x ad5693; // Create an object of the AD5693 library

const uint8_t DEBUG = 0;
const uint8_t CALIBRATION_MODE = 0;

// ---------- User configuration ----------
const uint8_t PIN_CS   = 10;   // CONVST/CS pin (any digital GPIO)
const uint8_t PIN_RST  = 9;    // RST pin (optional but recommended)
const uint8_t PIN_RVS  = 6;    // RVS (conversion-ready status) pin
const uint8_t PIN_CHRG_CTRL  = 5;    // charge control output pin

// SPI clock: datasheet allows up to 66.67 MHz for SPI
const uint32_t SPI_CLOCK_HZ =   40000000; // 40 MHz

SPISettings adsSPISettings(SPI_CLOCK_HZ, MSBFIRST, SPI_MODE0);

// Timing from the datasheet (Timing Requirements: Conversion Cycle,
// ADS8699 row): tconv = 5000 ns max. Used only as a safety-timeout
// ceiling for the RVS poll below now, not as the wait time itself.
const uint16_t T_CONV_US = 7;   // >= 5 us conversion time + margin
const uint16_t RVS_TIMEOUT_US = 50; // generous safety net; real tconv is ~5us

// ---------- Charge setpoint ----------
// Hard ceiling for SET commands. Set this to what your capacitor bank,
// IGBTs and probe (1300 V max) can safely take; anything above it is refused.
const float SETPOINT_MAX_V = 1000.0f;
// Setpoints below this count as "charging disabled": DAC at 0 V and the
// direct-control output held LOW.
const float SETPOINT_MIN_ACTIVE_V = 1.0f;
// The active setpoint in capacitor volts. Always starts at 0 V on boot.
// Change it with the SET command, not by editing this line.
float chargeSetpointV = 0.0f;

// If a value is below -10v, ignore it and wait for the next one...
const float MIN_VOLTAGE_THRESHOLD = -10;

// ---------- ADS8699 averaging configuration ----------
// NUM_AVG sets the fast control loop's latency: each batch takes roughly
// NUM_AVG x (one conversion + SPI read). Lower = faster cutoff response.
uint16_t NUM_AVG = 500;
const uint16_t NUM_AVG_MIN = 1;
const uint16_t NUM_AVG_MAX = 20000; // sanity ceiling for the 64-bit accumulator / loop time

// ---------- Slow-task rates ----------
// ADS1115: one "sweep" = one conversion on every channel in ADS1115_CHANNELS.
// Sweeps start at ADS1115_SWEEP_HZ; ADS1115_AVG sweeps are averaged before
// a new value is published (published rate = ADS1115_SWEEP_HZ / ADS1115_AVG).
uint16_t ADS1115_SWEEP_HZ = 100;
uint16_t ADS1115_AVG = 10;               // -> 10 Hz published, each a 10-sample average
// At 860 SPS a conversion takes ~1.16 ms; we don't touch the bus until this has passed.
const uint32_t ADS1115_CONV_WAIT_US = 1300;

uint16_t PRINT_HZ = 10;                  // Serial output rate
const uint32_t DAC_RETRY_MS = 100;       // retry interval if a DAC write fails

// ---------- ADS1115 channel map ----------
const uint8_t ADS1115_CHANNELS[] = {1, 3};
const uint8_t ADS1115_NUM_CH = sizeof(ADS1115_CHANNELS);
const uint8_t ADS1115_CH_DAC   = 1;
const uint8_t ADS1115_CH_PROBE = 3;

// ---------- DAC configuration ----------
float vref = 2.5000;
uint8_t gain = 2;   // gain of 2 means our span is 0-5V
// Target DAC output voltage (what the comparator sees). Set from the charge
// setpoint by applySetpoint(); dac_service() only writes to the chip when
// the resulting code changes.
float dacTargetVolts = 0.00f;
const float DAC_VERIFY_TOL_V = 0.010f;   // ADS1115 readback must be within this of the commanded voltage

// ADS8699 Calibration of ADC input voltage to calibrated multimeter
// Y = 0.9997*X + 9.895e-005 (cal performed 10/2/2026)
const float ADS8699_CAL_OFFSET = 0.00009895;
const float ADS8699_CAL_SCALE = 0.9997;

// ADS1115 Calibration of ADC input voltage to calibrated multimeter
//  Y = 1.000*X + 0.001057 (cal performed 10/2/2026)
const float ADS1115_CAL_OFFSET = 0.001057;
const float ADS1115_CAL_SCALE = 1.000;

// Probe Multiplier; used for measuring active HV differential probes.
// For measuring capacitor voltage, I'm using a 1300V diff probe with a multiplier of 500X
const uint16_t PROBE_MULTIPLIER = 500;

// Calibration for actual measured capacitor voltage
// Y = 0.9854*X + 0.1270
const float VDIV_CAL_OFFSET = 0.127;
const float VDIV_CAL_SCALE = 0.9854;

// ---------- Input range table (Table 7-3 / 7-4, VREF = 4.096 V) ----------
// (Kept above the first function: the Arduino IDE inserts auto-generated
// prototypes just before the first function, so custom types used in
// function signatures must be defined before it.)
enum ADS8699_Range : uint8_t {
  RANGE_PM_3VREF    = 0b0000, // ±12.288 V
  RANGE_PM_2p5VREF  = 0b0001, // ±10.24 V
  RANGE_PM_1p5VREF  = 0b0010, // ±6.144 V
  RANGE_PM_1p25VREF = 0b0011, // ±5.12 V
  RANGE_PM_0p625VREF= 0b0100, // ±2.56 V
  RANGE_0_3VREF     = 0b1000, // 0 to 12.288 V
  RANGE_0_2p5VREF   = 0b1001, // 0 to 10.24 V
  RANGE_0_1p5VREF   = 0b1010, // 0 to 6.144 V
  RANGE_0_1p25VREF  = 0b1011  // 0 to 5.12 V
};

// Positive/negative full-scale voltages for each range, VREF = 4.096 V
struct RangeInfo { float negFS; float posFS; };

///////////////////////////////////////////////////////////////////////////////
// SHARED STATE FOR SLOW TASKS
// (globals declared before any function that uses them)

// Latest published ADS1115 readings, calibrated, indexed by AIN number.
float ads1115_volts[4] = {0.0f, 0.0f, 0.0f, 0.0f};
bool ads1115_haveData = false;   // true once the first averaged set has been published
bool ads1115_newData = false;    // set on each publish, cleared by the consumer in loop()

int32_t lastDacCodeWritten = -1; // -1 = nothing written yet
bool dacSkipNextVerify = true;   // skip the averaging window that straddles a DAC change
bool dacVerifyOk = false;
float dacVerifyErrorV = 0.0f;

bool chargePinOn = false;        // last level written to PIN_CHRG_CTRL (for the status line)

///////////////////////////////////////////////////////////////////////////////
// AD5693 DAC FUNCTIONS
uint16_t voltageToDacCode(float voltage, float vref, uint8_t gain) {
  float maxCode = 65536.0;
  float code = (voltage / (vref * gain)) * maxCode;
  if (code > 65535.0) code = 65535.0;
  if (code < 0.0) code = 0.0;
  return (uint16_t)code;
}

// Inverse of voltageToDacCode(): the voltage the DAC should output for a given code.
float codeToVoltage(uint16_t code, float vref, uint8_t gain) {
  return vref * gain * ((float)code / 65536.0);
}

// Converts a desired capacitor voltage into the probe-output voltage the
// comparator should trip at (i.e. the DAC target), by inverting the probe
// multiplier and the probe calibration used for v_cap in loop().
// The DAC's own accuracy isn't calibrated here -- that's what the ADS1115
// verification is for.
float capVoltToDacVolts(float capVolts) {
  float v_div = (capVolts - VDIV_CAL_OFFSET) / VDIV_CAL_SCALE;
  return v_div / (float)PROBE_MULTIPLIER;
}

// Writes the DAC only when the target code differs from what was last
// successfully written. On failure, retries no more often than DAC_RETRY_MS
// so a disconnected DAC can't flood the bus or Serial.
void dac_service() {
  static elapsedMillis sinceFail = DAC_RETRY_MS;

  uint16_t code = voltageToDacCode(dacTargetVolts, vref, gain);
  if ((int32_t)code == lastDacCodeWritten) return;
  if (sinceFail < DAC_RETRY_MS) return;

  if (ad5693.writeUpdateDAC(code)) {
    lastDacCodeWritten = code;
    dacSkipNextVerify = true;   // the next published ADS1115 average may include pre-change samples
  } else {
    sinceFail = 0;
    Serial.println("Failed to update DAC.");
  }
}

// Compares the ADS1115's DAC-channel reading with the commanded DAC
// voltage. Called whenever a new averaged ADS1115 set is published.
void dac_verify() {
  if (lastDacCodeWritten < 0) { dacVerifyOk = false; return; }
  if (dacSkipNextVerify) { dacSkipNextVerify = false; return; }

  float expected = codeToVoltage((uint16_t)lastDacCodeWritten, vref, gain);
  dacVerifyErrorV = ads1115_volts[ADS1115_CH_DAC] - expected;
  dacVerifyOk = fabsf(dacVerifyErrorV) <= DAC_VERIFY_TOL_V;
}

///////////////////////////////////////////////////////////////////////////////
// CHARGE SETPOINT

bool chargeEnabled() {
  return chargeSetpointV >= SETPOINT_MIN_ACTIVE_V;
}

// The only place the setpoint changes. Updates the DAC target too, so the
// comparator and the direct control always use the same value.
void applySetpoint(float capVolts) {
  if (!(capVolts >= 0.0f)) capVolts = 0.0f;            // also catches NaN
  if (capVolts > SETPOINT_MAX_V) capVolts = SETPOINT_MAX_V;
  chargeSetpointV = capVolts;
  dacTargetVolts = chargeEnabled() ? capVoltToDacVolts(chargeSetpointV) : 0.0f;
}

///////////////////////////////////////////////////////////////////////////////
// SERIAL COMMANDS (non-blocking)
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

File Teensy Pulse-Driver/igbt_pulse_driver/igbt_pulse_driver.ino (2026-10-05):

/*
  OpenTMS IGBT pulse generator + gate-driver feedback monitor -- Teensy 4.1
  --------------------------------------------------------------------------
  Fires pulse trains to two 1SD418F2 gate drivers (one shared output pin, so
  both IGBTs of the two-switch flyback switch together) and checks each
  driver's fiber status/acknowledge line on every pulse.

  Expected driver behaviour (1SD418F2 datasheet):
    - ~450 ns after EACH edge of the command pulse (turn-on and turn-off),
      the status line gives an acknowledge pulse 0.7-1.8 us wide.
    - Status line active for > ~2 us = short-circuit / fault. After a fault
      the driver holds it active for its blocking time (~1 s).

  Detected anomalies (only anomalies are printed, never good pulses):
    FAULT  NO_ACK          no acknowledge after a rising or falling edge
    FAULT  SC_FAULT        status line active > FAULT_WIDTH_NS (short circuit / fault)
    FAULT  NOT_IDLE        status line already active when a pulse fired
    FAULT  IDLE_SC_FAULT   status line active > FAULT_WIDTH_NS between pulses
    FAULT  FAULT_HELD      status line held active > FAULT_HELD_MS (driver blocking)
    WARN   LATE_ACK        ack arrived later than ACK_DELAY_MAX_NS
    WARN   SHORT_ACK       ack narrower than ACK_WIDTH_MIN_NS
    WARN   LONG_ACK        ack wider than ACK_WIDTH_MAX_NS but below the fault threshold
    WARN   EXTRA_PULSE     unexpected status pulse during/just after a command pulse
    WARN   IDLE_GLITCH     short status pulse between command pulses
    WARN   TOO_MANY_EDGES  more status transitions than can be stored in one capture
    INFO   FAULT_CLEARED   a held fault line went idle again (with total duration)

  Fault response:
    - Any FAULT latches: LED on solid, safety relay (if wired) de-energized.
    - WARNs blink the LED briefly (or latch too, if TRIP_ON_WARNINGS = true).
    - Pulses KEEP FIRING regardless (STOP_FIRING_ON_FAULT = false) -- per request.
    - Send 'r' over Serial to clear the latch (only if both lines are idle),
      's' to print a status summary immediately.

  Timing: each pulse runs with interrupts disabled (~DWELL + 8 us) so the
  pulse width is exact and the status lines are sampled every ~50 ns using
  the CPU cycle counter.
*/

#include <Arduino.h>

#if !defined(__IMXRT1062__)
#error "This sketch is written for Teensy 4.x (uses ARM_DWT_CYCCNT and digitalReadFast timing)."
#endif

// Declared up front so the Arduino IDE doesn't auto-generate a C++-linkage
// prototype that would clash with the core's C-linkage weak symbol.
extern "C" void startup_middle_hook(void);

// ============================================================================
// PULSE PATTERN
// ============================================================================
// Tested IGBT ampacity at DWELL = 50
uint32_t DWELL = 60;                  // us, IGBT on-time per pulse
const uint32_t DWELL_MAX_US = 100;    // hard ceiling: DWELL is clamped to this no matter what
uint32_t INTERPULSE_DELAY = 40;       // ms, start-to-start spacing of pulses in a train (40 ms = 25 Hz)
uint32_t INTER_TRAIN_DELAY = 200;     // ms, extra gap added after the last pulse of a train
uint32_t PULSES_PER_TRAIN = 7;
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

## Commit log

2024-12-03 added Arduino sketch which I'm using in the SCR-based TMS pulse-generator
2024-12-19 added photos of newest coil assembly pre and post epoxy potting, a few pictures of giant capacitors, probs a picture of my janky workbench containing TMS V3 in all it's glory. Someday..... I promise 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
